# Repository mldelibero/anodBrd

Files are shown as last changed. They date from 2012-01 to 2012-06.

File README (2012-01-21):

This repo houses all of the important resources for the anodization board research project. It is part of a larger project at Case Western Reserve University that is attempting to create ultra-high energy density capacitors.

There have sofar been two main authors on this project:

Steven Ehret:
    Board design and layout
Michael DeLibero:
    Board validation and analysis
    Firmware code
    PC UI and data processing

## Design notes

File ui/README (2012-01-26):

This code communicates to the Board via USB.

It is responsible for:

configuring test modes
starting tests
receiving and saving data during tests
stopping tests

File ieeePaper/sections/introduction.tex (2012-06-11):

\section{Introduction}

Capacitors with high energy and power are essential for efficient management of electrical power.  Order of magnitude increases are desired for energy and power density. This may be possible with new self-repairing titanate dielectric capacitors using high surface area doped titanium and doped zirconium-titanium.  Anodizing at DC voltages forms a uniform dielectric film of doped titanium. The energy density of this dielectric is estimated to be on the order of 150J/$cm^3$ \cite{tiSponge}. This and the volume fraction of dielectric determines the energy density of the capacitor.

One of the major problems plaguing titanium electrolytic capacitors has been their high leakage currents \cite{tiCharHag}. In order to further research into titanium capacitors, custom anodization instrumentation has been developed to anodize and characterize a large number of candidate titanium capacitor materials. This instrumentation was necessary because conventional systems do not have the necessary dynamic range (1A-1nA measurement) or repeatability needed in this application.

\subsection{Anodization Process and Requirements}

Anodization is the act of growing an oxide layer (dielectric) on top of a metal anode. Dielectrics are beneficial because they allow capacitors to store more energy for a given electric field \cite{cwruEncDie}. The anodization process is preformed by connecting a voltage or current source to an anode and a cathode and immersing them in an electrolyte solution as shown in Fig. ~\ref{fig:anodSetup}

\begin{figure}[here]
\centering
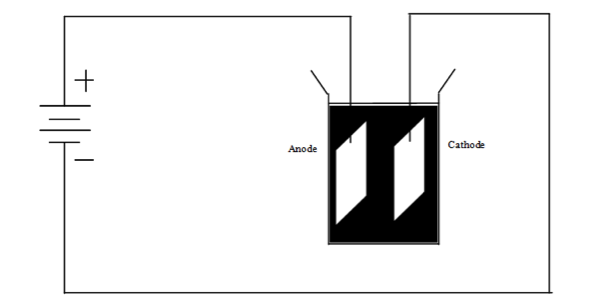
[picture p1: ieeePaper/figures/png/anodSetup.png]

\caption{Anodization Setup}
\label{fig:anodSetup}
\end{figure}

Referring to Fig. ~\ref{fig:anodSetup}, in the simplest case, the current transfer is an ionic transfer where the Ti anode reacts with $O_{2}$ to create a $TiO_{2}$ oxide layer. The reaction at the metal-oxide surface can be written as:

\begin{equation}
Ti + 0_2 => TiO_2 + 4e
\end{equation}
The titanium also reacts with the electrolyte solution to give off hydrogen:
\begin{equation}
Ti + 2H_20 => Ti0_2 + 4H
\end{equation}
This hydrogen reacts with the electrons at the cathode to create hydrogen gas and complete the ionic circuit.
\begin{equation}
4H + 4e => 2H_2
\end{equation}

This process is very similar to anodizing aluminum. For an explanation of that process visit \cite{cwruEncAlanod}.

Since the rate of oxide formation is dependent on the charge transport into the anode during anodization \cite{tiMinit}, a current source was selected. A typical anodization process with a current source will see the current and voltage progress as in Fig. ~\ref{fig:anodCurve}.

\begin{figure}[here]
\centering
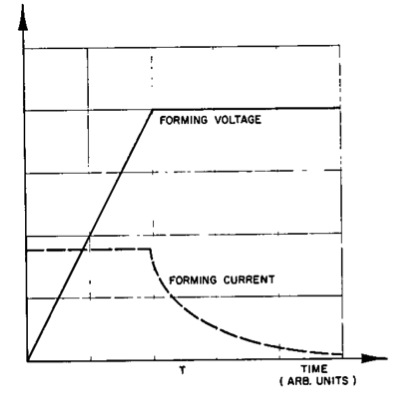
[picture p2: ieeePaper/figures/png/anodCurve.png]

\caption{Anodization Curve \cite{tiMinit}}
\label{fig:anodCurve}
\end{figure}

Our typical anodization tests work with a constant current of 20mA and a forming voltage of 30V. The anodization reaches the forming voltage in periods on the order of 30 seconds. The forming voltage then remains constant while the leakage current decreases over  a much longer time period (on the order of 24 hours) to currents on the order of 1 uA or less. The exact times and values are dependent upon the material and the size of the electrode.

If a constant current is introduced, the voltage will (ideally) rise linearly with time. This will happen until the anode reaches the compliance voltage, at which point the current through the DUT will begin to drop off until it reaches the leakage current of the unpackaged capacitor.

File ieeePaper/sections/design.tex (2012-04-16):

\begin{figure}[here]
\centering

\caption{Overall System Block Diagram}
\label{fig:blockDiagram}
\end{figure}

\subsection{Computer Control and Data Acquisition}

The user sets the test parameters of current, voltage compliance, and testing time. The anodization is then controlled by a set of Python scripts, which appropriately configure the hardware and control the data logging. Voltage and current measurements are sampled at a constant, high rate and all data is recorded. However, once the electrode has reached the forming voltage and the (leakage) current is slowly decreasing over time the data measurements are subsampled, and only a fraction of the sampled data is preserved.

\subsection{Current Source}

An ideal current source has the ability to output a constant, DC, current to any load with infinite voltage compliance. This ability makes a current source an attractive tool to use in anodization due to its ability to tightly control the rate of oxide growth on the anode.

\begin{figure}[here]
\centering
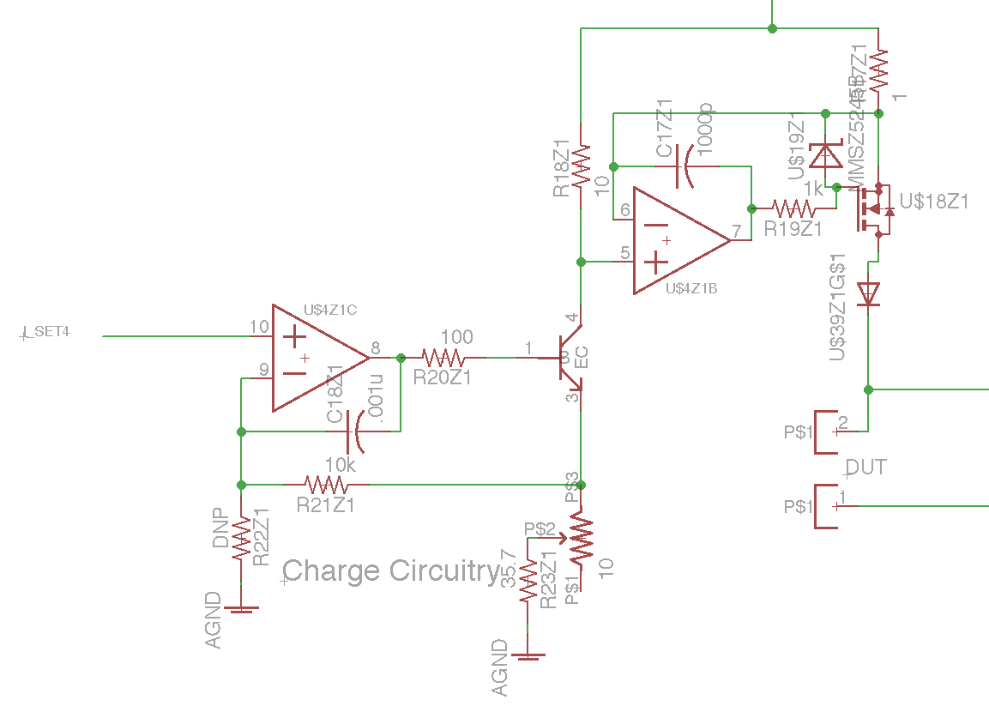
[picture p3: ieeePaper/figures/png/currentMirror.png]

\caption{Current Control Circuitry}
\label{fig:currentMirror}
\end{figure}

The current source implementation (Fig. ~\ref{fig:currentMirror}) was chosen around an op-amp based current mirror. The op-amp on the left, U4Z1C, is used to set and regulate the current through R23. This current functions as the reference current on the left leg of the current mirror. The op-amp on the right, U4Z1B, forces the voltage drop across $R_{17}$ and $R_{18}$ to be the same, causing the current in the right leg to go as:

\begin{equation}
I_2 = I_1*R_{18}/R_{17}
\end{equation}

With the values chosen in this design, this equates to a 10x current amplification from the reference to the current output. The adjustable supply voltage is applied to the node connecting resistors $R_{17}$ and $R_{18}$. The current source will be able supply a constant current up to an effective compliance voltage of the supply voltage minus the voltage drops of $R_{17}$, the pass transistor, and the protection diode.

The real current source has several practical limitations that provide less than ideal performance. 

\begin{enumerate}
\item Pass transistor power rating
\item Digitization of current settings
\item Slight nonlinearity due to the pass diode
\end{enumerate}

\begin{figure}[here]
\centering
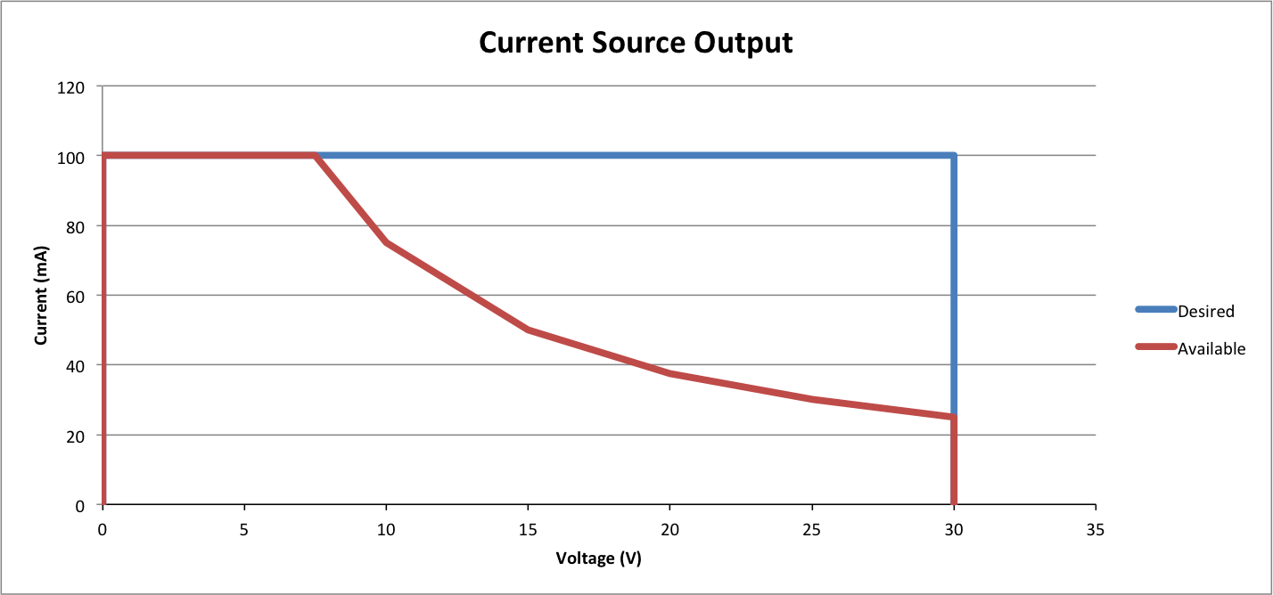
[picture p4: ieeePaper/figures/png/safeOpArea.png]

\caption{Current Source: Safe Operating Area}
\label{fig:safeOpArea}
\end{figure}

The safe operating area (Fig.  ~\ref{fig:safeOpArea}) is smaller than the desired operating output of 30V at 100mA. This difference comes from the limitations in the power dissipation of the pass transistor, U18Z1, in Fig. ~\ref{fig:currentMirror}. Assuming the worse case scenario of a short on the output, the allowable output current for a given voltage compliance can be found as:

\begin{equation}
I_{out} = P_{rating} / V_{comp}
\end{equation}

The current source operates by controlling the gate voltage of U18Z1 in Fig. ~\ref{fig:currentMirror}) ensure a constant current as the voltage on the DUT changes. Ideally, the source would be able to respond to a change in load impedance instantaneous to keep the current output constant. The real current source of Fig. ~\ref{fig:currentMirror} is limited by the Gain Bandwidth Product of the U4X1B (1.8Mhz). This limitation is of little concern, as the op-amp is still much faster then the fastest load change expected (See Section:\ref{DUT})

The ideal current source has the ability to output any desired current over its range with infinite precision. The current source in this design is limited in this regard by the discretization error of setting the current. Referring to (Fig. ~\ref{fig:currentMirror}) the signal $i_{set4}$ is used as a control signal to set the reference current in the device. This signal is controlled by a Microchip MCP4812 10-bit DAC. A first approximation of the discretization uncertainty in selecting DAC outputs can be found by:

\begin{equation}
U = Vi_{set} /(2n-1) / (R_{23} + R_{pot}) *(R_{18}/R_{17})
\end{equation}

Which yields an uncertainty in the current output of +/- 0.5mA. Calibration can eliminate this error for a single current output, but all other outputs will be in error by as much as the uncertainty.

The protection diode, U39, in (Fig. ~\ref{fig:currentMirror}) has the effect of increasing the voltage compliance as the current drops off after anodization. Looking at a standard diode curve, the voltage drop across the diode is roughly a constant 0.7V for high currents and exponentially diminishes towards zero as the current decreases. The tests are designed to not only anodize, but also continue to measure the long-term leakage current afterwards. This means that the current draw will decrease to the nA range, causing the effective voltage compliance to increase to about a diode drop above its anodization level. This affect will need to be considered during the analysis of the anodization data.

\subsection{DUT}
\label{DUT}

The device under test is typically a titanium anode to be anodized or a titanium capacitor. The device is able to operate with resistive loads and any capacitive loads (with capacitance large enough for the system to be able to respond.

\subsection{Current and Voltage Measurements}
\label{Current and Voltage Measurements}

The second part of the instrumentation is the measurement circuitry. An ideal measurement system would have no error or time delay when measuring the signal. It would also be able to perfectly reconstruct the signal for post analysis. 

\begin{figure}[here]
\centering
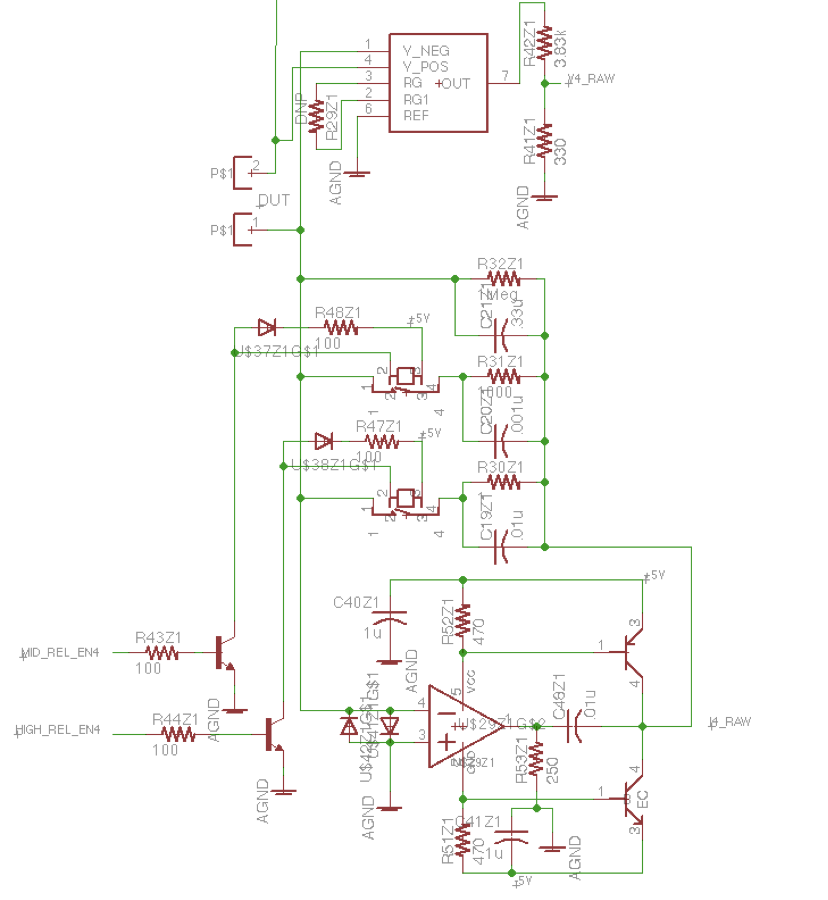
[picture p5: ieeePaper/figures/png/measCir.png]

\caption{Measurement Circuitry}
\label{fig:measCir}
\end{figure}

The measurement circuitry (Fig. ~\ref{fig:measCir}) implemented consists of two different parts, voltage and current measurements. The voltage of the DUT is measured differentially by an Analog Device’s AD8220 JFET instrumentation amplifier. This output is scaled and then sent to a 12-bit DAC. The current through the DUT is measure from a low side measurement topology known and a transimpedance amplifier. The amplifier creates a virtual ground at the negative terminal of the op-amp, U39, that allows for a current reading without subjecting the measurement circuitry to a high voltage and without floating the bottom of the DUT above ground.

Since it is desirable the measure both the anodization current and the leakage current, a basic transimpedance amplifier design was modified to include three switched feedback paths. This allows the current measurement to measure currents over eight orders of magnitude. The circuitry can handle currents from 10nA to 100mA. The three current ranges are listed in Table:~\ref{tab:dacRes}.

The real measurement circuitry has several practical limitations that limit it from performing ideally. Both the differential amplifier and the transimpedance amplifier send their signals to 6-pole Sallen-Key filters. These filters have a cutoff frequency of 10kHz\cite{sThesis} in order to filter out high frequency harmonics and other undesirable noise. Any signals higher than this will be severely attenuated in the captured data.

The DACs inject digitization errors into the measurement signals. They are able to measure signals with resolutions shown in Table:~\ref{tab:dacRes}.

\begin{table}[here]
\renewcommand{\arraystretch}{1.3}
\caption{DAC Resolution}
\label{tab:dacRes}
\centering
\begin{tabular}{c|c|c}
\hline
\bfseries Resolution & \bfseries Full Scale Measurement & \bfseries Comment\\
\hline\hline
7.32mV & 30V & \\
\hline
.098mA & 100mA & Hi Current (1A-1mA)\\
\hline
.98uA & 1mA & Med Current (1mA-1uA) \\
\hline
.98nA & 1uA & Lo Current (1uA-1nA)\\
\hline
\end{tabular}
\end{table}

Once the data is collected by the microcontroller, it is sent to a PC via USB for further analysis. The data is sampled by the ADCs at a configurable baud rate and transferred to the PC at a rate of 2Mbaud. This allows for maximum flexibility on the PC side, where any data coming in at a rate greater than what is desired can simply be discarded.

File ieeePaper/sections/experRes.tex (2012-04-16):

\section{Experimental Results}
Typical results from early materials can be found it Fig. 7. For additional data and complete testing curves, see \cite{sThesis} and \cite{mThesis}.

Since the circuitry has control over the output current and compliance voltage, it sets a limit for the maximum power allowed to be dissipated in its last pass transistor. This worst case operating method ensures that data taken of an unknown device will not damage the circuitry.
\begin{figure}[here]
\centering
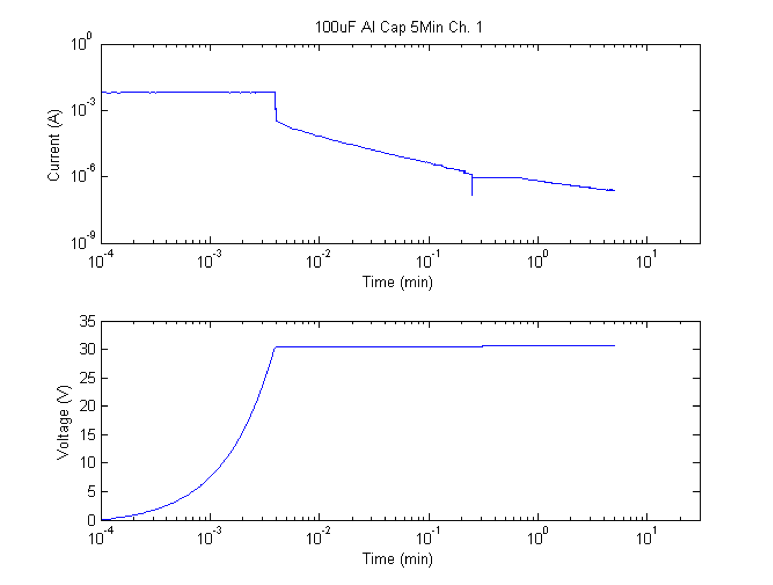
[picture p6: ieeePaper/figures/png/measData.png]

\caption{Typical Results}
\label{fig:measData}
\end{figure}

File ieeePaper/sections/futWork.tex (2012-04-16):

\section{Future Work}

Although this circuit functions to within its desired specifications, there are several improvements that can be made to achieve tighter control and greater accuracy.

\subsection{Safe Operating Area}

As discussed in Section:\ref{Current and Voltage Measurements} and seen in Fig:\ref{fig:safeOpArea}, the safe operating area of this circuitry is less then ideal. Even though the safe operating area contains the most commonly desired output conditions in the discussed experiments (20mA at 30V), it will need to be increased to accommodate higher current outputs.

A proposed way to achieve this increase is to create a software control loop using the existing circuitry. If the microcontroller limits the power dissipated in the last pass transistor while not affecting the DUT, this system can achieve a much greater safe operating area. Since the voltage across and current through the last pass transistor can be known at all times, power can be limited by the circuitry. The voltage at the top of the pass transistor can be estimated to be the compliance voltage set by the circuitry. During circuit operation, the voltage at the bottom of the pass transistor and current through are continuously measured by the microcontroller. Since anodization curves change on the order of $1 V/s$ (30V in 30 seconds), it is feasible to do a software controlled compensation loop. The microcontroller can set a constant current and ramp up the compliance voltage just above the voltage load. This will minimize the power dissipated in the last pass transistor and greatly increase the safe operating area of the circuitry.

\subsection{Schematic}

There are several improvements that could be made to the current schematic that would improve the overall design of the system. The circuitry uses 3 pass transistors with the last one transistor being undersized. The compliance voltage section could be redesigned in order to lower the number of pass elements and increase their power ratings. This will let the device supply currents to a wider variety of loads, without needing to use the technique described in the previous section.

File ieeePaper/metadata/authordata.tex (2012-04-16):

\newcommand{\gettitle}{Instrumentation For The Anodization and Characterization of Titanium Electrodes for Electrolytic Capacitors}

\newcommand{\getauthor}{M. DeLibero, Student Member, IEEE, S. Ehret, Member, IEEE, and F. Merat, Senior Member, IEEE}

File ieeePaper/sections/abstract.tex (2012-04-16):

\begin{abstract}
This paper presents a custom circuit for controlling the anodization of titanium capacitors and characterizing their performance. The circuitry provides a constant current source of 0-100mA up to a compliance voltage of 30V. The system can monitor and record leakage currents down to 10 nA over periods of up to 24 hours. Typical results obtained using sputtered titanium-zirconium capacitors are presented.
\end{abstract}

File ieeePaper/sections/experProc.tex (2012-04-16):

\section{Experimental Procedure}
The experimental setup to anodize the anode of a titanium capacitor with the aforementioned circuitry is as follows. The anode sample is prepared by cleaning the surface oxide off with a chemical bath. It is then placed in a beaker of anodizing solution. The current source is connected to the DUT and acts as both a current source and data logger until the test is finished and the current through the DUT has dropped to the leakage current.

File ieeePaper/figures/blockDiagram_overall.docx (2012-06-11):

DUT

PC

Current Source

Current Sense

Voltage Sense

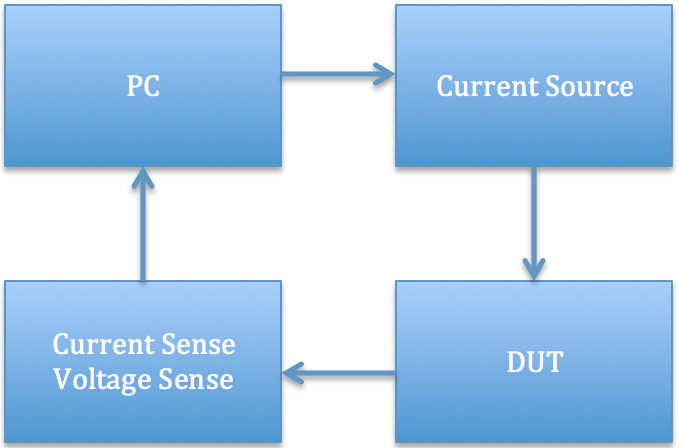
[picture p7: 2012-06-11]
ieeePaper/figures/blockDiagram.png

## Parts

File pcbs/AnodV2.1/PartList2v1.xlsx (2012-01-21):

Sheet: Digikey
Index | Quantity | Part Number | Value | Description | Customer Reference/Number Required per Board | Backorder Quantity | Unit Price | Extended Price |  | Need | Quantity
1 | 2 | 768-1101-1-ND (http://search.digikey.com/scripts/DkSearch/dksus.dll?Detail&itemSeq=102184557&uq=634458068631601009) |  | IC HS USB TO UART/FIFO 48LQFP | 1 | 0 | 4.25 | $8.50 | U5 | 2 | 2
2 | 5 | MCP4812-E/MS-ND (http://search.digikey.com/scripts/DkSearch/dksus.dll?Detail&itemSeq=102184565&uq=634458068631601009) |  | DAC 10BIT DUAL SPI/VREF 8MSOP | 4 | 0 | 2.3 | $11.50 |  | 0
3 | 8 | HE127-ND (http://search.digikey.com/scripts/DkSearch/dksus.dll?Detail&itemSeq=102184570&uq=634458068631601009) |  | RELAY REED SPST SIP SW 5V | 8 | 0 | 3.09 | $24.72 | U27 | 2 | 2
4 | 5 | NCP1117DT33GOS-ND (http://search.digikey.com/scripts/DkSearch/dksus.dll?Detail&itemSeq=102184588&uq=634458068631601009) |  | IC REG LDO 3.3V DPAK | 1 | 0 | 0.52 | $2.60 | U | 0
5 | 4 | AD8638ARJZ-REEL7CT-ND (http://search.digikey.com/scripts/DkSearch/dksus.dll?Detail&itemSeq=102184594&uq=634458068631601009) |  | IC OPAMP CHOPPER R-R SOT23-5 | 4 | 0 | 3.81 | $15.24 | U | 0
6 | 10 | 490-2872-ND (http://search.digikey.com/scripts/DkSearch/dksus.dll?Detail&itemSeq=102184612&uq=634458068631601009) |  | TRIMMER 10 OHM 0.5W TH | 8 | 0 | 1.07 | $10.70 | no longer used
7 | 10 | DMN3115UDMDICT-ND (http://search.digikey.com/scripts/DkSearch/dksus.dll?Detail&itemSeq=102184617&uq=634458068631601009) |  | MOSFET N-CH 30V 3.2A SOT-26 | 4 | 0 | 0.462 | $4.62 | U24,DS31187 | 0
8 | 10 | 296-7423-1-ND (http://search.digikey.com/scripts/DkSearch/dksus.dll?Detail&itemSeq=102184623&uq=634458068631601009) |  | IC OPAMP GP 635KHZ QUAD 14TSSOP | 8 | 0 | 1.17 | $11.70 |  | 0
9 | 4 | AD8220ARMZ-ND (http://search.digikey.com/scripts/DkSearch/dksus.dll?Detail&itemSeq=102184630&uq=634458068631601009) |  | IC AMP INST JFET R-R 15MA 8MSOP | 4 | 0 | 6.86 | $27.44 |  | 0
10 | 25 | ES1G-TPCT-ND (http://search.digikey.com/scripts/DkSearch/dksus.dll?Detail&itemSeq=102184689&uq=634458068631601009) |  | DIODE FAST REC 1A 400V DO214AC | 18 | 0 | 0.302 | $7.55 | U38 | 0
11 | 3 | ZXRE1004DFCT-ND (http://search.digikey.com/scripts/DkSearch/dksus.dll?Detail&itemSeq=102184694&uq=634458068631601009) |  | IC VREF 1.22V 20MA 1% SOT23-3 | 1 | 0 | 1.33 | $3.99 |  | 0
12 | 2 | CTX691CT-ND (http://search.digikey.com/scripts/DkSearch/dksus.dll?Detail&itemSeq=102184701&uq=634458068631601009) |  | OSC CLOCK 16.000000 MHZ 3.3V SMD | 1 | 0 | 3.92 | $7.84 |  | 0
13 | 1 | 285-1822-ND (http://search.digikey.com/scripts/DkSearch/dksus.dll?Detail&itemSeq=102184707&uq=634458068631601009) |  | POWER SUPPLY 36V 1.4A SGL OUTPUT | 1 | 0 | 29.93 | $29.93 |  | 0
14 | 5 | 296-21390-1-ND (http://search.digikey.com/scripts/DkSearch/dksus.dll?Detail&itemSeq=102184724&uq=634458068631601009) |  | IC VOLT REG POS ADJ 1.5A D2PAK-3 | 1 | 0 | 1.06 | $5.30 |  | 0
15 | 5 | LP38690DT-5.0-ND (http://search.digikey.com/scripts/DkSearch/dksus.dll?Detail&itemSeq=102184731&uq=634458068631601009) |  | IC REG LDO 1A 5.0V TO-252 | 1 | 0 | 1.64 | $8.20 |  | 0
16 | 2 | CP-1060-ND (http://search.digikey.com/scripts/DkSearch/dksus.dll?Detail&itemSeq=102184739&uq=634458068631601009) |  | CONN CIRCULAR DIN 6 PIN MALE | 1 | 0 | 1.6 | $3.20 |  | 0
17 | 2 | CP-2360-ND (http://search.digikey.com/scripts/DkSearch/dksus.dll?Detail&itemSeq=102184745&uq=634458068631601009) |  | CONN DIN 6 PIN FEMALE PCB | 1 | 0 | 1.37 | $2.74 |  | 0
18 | 5 | LM2990S-5.0-ND (http://search.digikey.com/scripts/DkSearch/dksus.dll?Detail&itemSeq=102184747&uq=634458068631601009) |  | IC REGULATOR NEG LDO TO-263 | 1 | 0 | 3.58 | $17.90 |  | 0
19 | 20 | 490-1718-1-ND (http://search.digikey.com/scripts/DkSearch/dksus.dll?Detail&itemSeq=102185015&uq=634458068631601009) |  | CAP CER 10UF 6.3V 20% X5R 0805 |  | 0 | 0.227 | $4.54 |  | 0
20 | 10 | SI2319DS-T1-E3CT-ND (http://search.digikey.com/scripts/DkSearch/dksus.dll?Detail&itemSeq=102185021&uq=634458068631601009) |  | MOSFET P-CH 40V 2.3A SOT23-3 | 8 | 0 | 0.86 | $8.60 | U18 | 5 | 5
21 | 12 | 2SD1758TLRCT-ND (http://search.digikey.com/scripts/DkSearch/dksus.dll?Detail&itemSeq=102185024&uq=634458068631601009) |  | TRANS NPN 32V 2A SOT-428 | 12 | 0 | 0.77 | $9.24 | U54 | 4 | 4
22 | 4 | 2SB1182TLRCT-ND (http://search.digikey.com/scripts/DkSearch/dksus.dll?Detail&itemSeq=102185030&uq=634458068631601009) |  | TRANSISTOR PNP 32V 2A SOT-428 | 4 | 0 | 1.05 | $4.20 | U55 | 4 | 4
23 | 10 | 493-1341-ND (http://search.digikey.com/scripts/DkSearch/dksus.dll?Detail&itemSeq=102185033&uq=634458068631601009) | 100 uF | CAP ALUM 100UF 50V 20% RADIAL | 3 | 0 | 0.215 | $2.15 |  | 0
24 | 50 | 490-1496-1-ND (http://search.digikey.com/scripts/DkSearch/dksus.dll?Detail&itemSeq=102185041&uq=634458068631601009) | 1200 pF | CAP CER 1200PF 50V 10% X7R 0603 |  | 0 | 0.054 | $2.70 |  | 0
25 | 50 | 445-5189-1-ND (http://search.digikey.com/scripts/DkSearch/dksus.dll?Detail&itemSeq=102202420&uq=634458100422898435) | 15000 pF | CAP CER 15000PF 50V X7R 0603 | 8 | 0 | 0.0376 | $1.88 | C55 | 0
26 | 100 | 490-1512-1-ND (http://search.digikey.com/scripts/DkSearch/dksus.dll?Detail&itemSeq=102185106&uq=634458068631601009) | 10000 pF | CAP CER 10000PF 50V 10% X7R 0603 |  | 0 | 0.015 | $1.50 |  | 0
27 | 250 | 490-1494-1-ND (http://search.digikey.com/scripts/DkSearch/dksus.dll?Detail&itemSeq=102185111&uq=634458068631601009) | 1000 pF | CAP CER 1000PF 50V 10% X7R 0603 |  | 0 | 0.01196 | $2.99 |  | 0
28 | 100 | 490-1500-1-ND (http://search.digikey.com/scripts/DkSearch/dksus.dll?Detail&itemSeq=102185121&uq=634458068631601009) | 2200 pF | CAP CER 2200PF 50V 10% X7R 0603 |  | 0 | 0.0283 | $2.83 |  | 0
29 | 250 | 490-1568-1-ND (http://search.digikey.com/scripts/DkSearch/dksus.dll?Detail&itemSeq=102185126&uq=634458068631601009) | .1 uF | CAP CER .1UF 50V Y5V 0603 |  | 0 | 0.01724 | $4.31 |  | 0
30 | 100 | 490-1543-1-ND (http://search.digikey.com/scripts/DkSearch/dksus.dll?Detail&itemSeq=102185132&uq=634458068631601009) | 1.0 uF | CAP CER 1.0UF 10V 10% X5R 0603 |  | 0 | 0.0336 | $3.36 |  | 0
31 | 10 | 445-5169-1-ND (http://search.digikey.com/scripts/DkSearch/dksus.dll?Detail&itemSeq=102185141&uq=634458068631601009) | 3.3 uF | CAP CER 3.3UF 10V X5R 0603 |  | 0 | 0.33 | $3.30 | C14 | 5 | 5
32 | 2 | 929400E-01-36-ND (http://search.digikey.com/scripts/DkSearch/dksus.dll?Detail&itemSeq=102185148&uq=634458068631601009) |  | CONN HEADER .100 SNGL STR 36POS | 18 | 0 | 1.8 | $3.60 |  | 0
33 | 10 | 587-1603-1-ND (http://search.digikey.com/scripts/DkSearch/dksus.dll?Detail&itemSeq=102185154&uq=634458068631601009) | 10 uH | INDUCTOR 10UH 20% 0805 SMD | 1 | 0 | 0.188 | $1.88 |  | 0
34 | 10 | 240-2370-1-ND (http://search.digikey.com/scripts/DkSearch/dksus.dll?Detail&itemSeq=102185159&uq=634458068631601009) |  | FERRITE 1A 60 OHM 0603 SMD | 4 | 0 | 0.081 | $0.81 |  | 0
35 | 20 | MMSZ5245B-TPMSCT-ND (http://search.digikey.com/scripts/DkSearch/dksus.dll?Detail&itemSeq=102185163&uq=634458068631601009) |  | DIODE ZENER 500MW 15V SOD123 | 12 | 0 | 0.255 | $5.10 | U33, | 0
36 | 30 | DSS4140UDICT-ND (http://search.digikey.com/scripts/DkSearch/dksus.dll?Detail&itemSeq=102185170&uq=634458068631601009) |  | TRANS BIPOLAR NPN 40V SOT-323 | 20 | 0 | 0.4 | $12.00 | U17 | 0
37 | 10 | 497-1958-1-ND (http://search.digikey.com/scripts/DkSearch/dksus.dll?Detail&itemSeq=102185182&uq=634458068631601009) |  | IC AMP QUAD BIPOLAR OP LP 14SOIC | 4 | 0 | 0.986 | $9.86 |  | 0
38 | 10 | RFD3055LE-ND (http://search.digikey.com/scripts/DkSearch/dksus.dll?Detail&itemSeq=102185192&uq=634458068631601009) |  | MOSFET N-CH 60V 11A I-PAK | 4 | 0 | 0.702 | $7.02 |  | 0
39 | 10 | WSLB-.10CT-ND (http://search.digikey.com/scripts/DkSearch/dksus.dll?Detail&itemSeq=102185200&uq=634458068631601009) | 0.10 O | RES .10 OHM 1/4W 1% 0805 SMD |  | 0 | 0.91 | $9.10 |  | 0
40 | 10 | RMCF0603FT1R00CT-ND (http://search.digikey.com/scripts/DkSearch/dksus.dll?Detail&itemSeq=102185208&uq=634458068631601009) | 1 O | RES TF 1 OHM 1% 0.1W 0603 |  | 0 | 0.025 | $0.25 | no longer used | 0
41 | 10 | P10.0HCT-ND (http://search.digikey.com/scripts/DkSearch/dksus.dll?Detail&itemSeq=102185213&uq=634458068631601009) | 10.0 O | RES 10.0 OHM 1/10W 1% 0603 SMD |  | 0 | 0.04 | $0.40 |  | 0
42 | 100 | P100HCT-ND (http://search.digikey.com/scripts/DkSearch/dksus.dll?Detail&itemSeq=102185215&uq=634458068631601009) | 100 O | RES 100 OHM 1/10W 1% 0603 SMD |  | 0 | 0.0105 | $1.05 |  | 0
43 | 50 | P330HCT-ND (http://search.digikey.com/scripts/DkSearch/dksus.dll?Detail&itemSeq=102185220&uq=634458068631601009) | 330 O | RES 330 OHM 1/10W 1% 0603 SMD |  | 0 | 0.0138 | $0.69 |  | 0
44 | 50 | P10.0KHCT-ND (http://search.digikey.com/scripts/DkSearch/dksus.dll?Detail&itemSeq=102185222&uq=634458068631601009) | 10.0 kO | RES 10.0K OHM 1/10W 1% 0603 SMD |  | 0 | 0.0138 | $0.69 |  | 0
45 | 50 | P100KHCT (http://search.digikey.com/scripts/DkSearch/dksus.dll?Detail&itemSeq=102185223&uq=634458068631601009) | 100 kO | RES 100K OHM 1/10W 1% 0603 SMD |  | 0 | 0.0138 | $0.69 |  | 0
46 | 10 | P12.0KHCT-ND (http://search.digikey.com/scripts/DkSearch/dksus.dll?Detail&itemSeq=102185237&uq=634458068631601009) | 12.0 kO | RES 12.0K OHM 1/10W 1% 0603 SMD |  | 0 | 0.04 | $0.40 |  | 0
47 | 50 | P124HCT-ND (http://search.digikey.com/scripts/DkSearch/dksus.dll?Detail&itemSeq=102185243&uq=634458068631601009) | 124 O | RES 124 OHM 1/10W 1% 0603 SMD |  | 0 | 0.0138 | $0.69 |  | 0
48 | 50 | P294HCT-ND (http://search.digikey.com/scripts/DkSearch/dksus.dll?Detail&itemSeq=102185248&uq=634458068631601009) | 294 O | RES 294 OHM 1/10W 1% 0603 SMD |  | 0 | 0.0138 | $0.69 |  | 0
49 | 50 | P470HCT-ND (http://search.digikey.com/scripts/DkSearch/dksus.dll?Detail&itemSeq=102185253&uq=634458068631601009) | 470 O | RES 470 OHM 1/10W 1% 0603 SMD |  | 0 | 0.0138 | $0.69 |  | 0
50 | 50 | P249HCT-ND (http://search.digikey.com/scripts/DkSearch/dksus.dll?Detail&itemSeq=102185257&uq=634458068631601009) | 249 O | RES 249 OHM 1/10W 1% 0603 SMD |  | 0 | 0.0138 | $0.69 |  | 0
51 | 50 | P14.7KHCT-ND (http://search.digikey.com/scripts/DkSearch/dksus.dll?Detail&itemSeq=102185260&uq=634458068631601009) | 14.7 kO | RES 14.7K OHM 1/10W 1% 0603 SMD |  | 0 | 0.0138 | $0.69 |  | 0
52 | 50 | P14.0KHCT-ND (http://search.digikey.com/scripts/DkSearch/dksus.dll?Detail&itemSeq=102185263&uq=634458068631601009) | 14.0 kO | RES 14.0K OHM 1/10W 1% 0603 SMD |  | 0 | 0.0138 | $0.69 |  | 0
53 | 50 | P1.00KHCT-ND (http://search.digikey.com/scripts/DkSearch/dksus.dll?Detail&itemSeq=102185266&uq=634458068631601009) | 1.00 kO | RES 1.00K OHM 1/10W 1% 0603 SMD |  | 0 | 0.0138 | $0.69 |  | 0
54 | 50 | P20.5KHCT-ND (http://search.digikey.com/scripts/DkSearch/dksus.dll?Detail&itemSeq=102185268&uq=634458068631601009) | 20.5 kO | RES 20.5K OHM 1/10W 1% 0603 SMD |  | 0 | 0.0138 | $0.69 |  | 0
55 | 50 | P2.94KHCT-ND (http://search.digikey.com/scripts/DkSearch/dksus.dll?Detail&itemSeq=102185272&uq=634458068631601009) | 2.94 kO | RES 2.94K OHM 1/10W 1% 0603 SMD |  | 0 | 0.0138 | $0.69 | R69 | 0
56 | 50 | P3.57KHCT-ND (http://search.digikey.com/scripts/DkSearch/dksus.dll?Detail&itemSeq=102185277&uq=634458068631601009) | 3.57 kO | RES 3.57K OHM 1/10W 1% 0603 SMD |  | 0 | 0.0138 | $0.69 | R72 | 0
57 | 50 | P10.2KHCT-ND (http://search.digikey.com/scripts/DkSearch/dksus.dll?Detail&itemSeq=102185281&uq=634458068631601009) | 10.2 kO | RES 10.2K OHM 1/10W 1% 0603 SMD |  | 0 | 0.0138 | $0.69 |  | 0
58 | 50 | P35.7HCT-ND (http://search.digikey.com/scripts/DkSearch/dksus.dll?Detail&itemSeq=102185286&uq=634458068631601009) | 35.7 O | RES 35.7 OHM 1/10W 1% 0603 SMD |  | 0 | 0.0138 | $0.69 |  | 0
59 | 50 | P68.1HCT-ND (http://search.digikey.com/scripts/DkSearch/dksus.dll?Detail&itemSeq=102185295&uq=634458068631601009) | 68.1 O | RES 68.1 OHM 1/10W 1% 0603 SMD |  | 0 | 0.0138 | $0.69 |  | 10 | 10
60 | 50 | P2.00KHCT-ND (http://search.digikey.com/scripts/DkSearch/dksus.dll?Detail&itemSeq=102185299&uq=634458068631601009) | 2.00 kO | RES 2.00K OHM 1/10W 1% 0603 SMD |  | 0 | 0.0138 | $0.69 |  | 0
61 | 50 | P3.83KHCT-ND (http://search.digikey.com/scripts/DkSearch/dksus.dll?Detail&itemSeq=102185302&uq=634458068631601009) | 3.83k | RES 3.83K OHM 1/10W 1% 0603 SMD |  | 0 | 0.0138 | $0.69 |  | 0
62 | 50 | P4.42KHCT-ND (http://search.digikey.com/scripts/DkSearch/dksus.dll?Detail&itemSeq=102185309&uq=634458068631601009) | 4.42 kO | RES 4.42K OHM 1/10W 1% 0603 SMD |  | 0 | 0.0138 | $0.69 |  | 0
63 | 50 | P7.87KHCT-ND (http://search.digikey.com/scripts/DkSearch/dksus.dll?Detail&itemSeq=102185313&uq=634458068631601009) | 7.87 kO | RES 7.87K OHM 1/10W 1% 0603 SMD |  | 0 | 0.0138 | $0.69 |  | 0
64 | 50 | 541-3.57HHCT-ND (http://search.digikey.com/scripts/DkSearch/dksus.dll?Detail&itemSeq=102185316&uq=634458068631601009) | 3.57 O | RES 3.57 OHM 1/10W 1% 0603 SMD |  | 0 | 0.0436 | $2.18 |  | 0
65 | 1 | 151-1081-ND (http://search.digikey.com/scripts/DkSearch/dksus.dll?Detail&itemSeq=102185319&uq=634458068631601009) |  | CONN USB JACK TYPE B HORIZON R/A | 1 | 0 | 0.96 | $0.96 |  | 0
66 | 10 | 478-4086-1-ND (http://search.digikey.com/scripts/DkSearch/dksus.dll?Detail&itemSeq=102185485&uq=634458068631601009) | 10uF | CAP TANT LOWESR 10UF 10V 20% SMD | 2 | 0 | 0.326 | $3.26 | C1, C3 | 5 | 5
67 | 5 | SW336-ND (http://search.digikey.com/scripts/DkSearch/dksus.dll?Detail&itemSeq=102201465&uq=634458068631601009) |  | SWITCH SLIDE 3P 3POS EYELET TERM | 1 |  |  |  |  | 0
68 |  | P1.00MHCT-ND (http://search.digikey.com/us/en/products/ERJ-3EKF1004V/P1.00MHCT-ND/198072) | 1 MO | RES 1.00M OHM 1/10W 1% 0603 SMD | 2 |  |  |  | R32 | 0
69 |  | 490-3294-1-ND | .33 uF | Cap CER .33uF |  |  |  |  | C21 | 2 | 100
70 |  | P442HCT-ND (http://search.digikey.com/us/en/products/ERJ-3EKF4420V/P442HCT-ND/198392) | 442 O | RES 442 |  |  |  |  |  | 0
 |  | RHM9.10AECT-ND (http://search.digikey.com/us/en/products/ESR10EZPF9R10/RHM9.10AECT-ND/1983890) | 9.10 O | RES 9.10 OHM 1/4W 1% 0805 SMD | 2 |  |  |  | R30 | 10 | 10
 |  | 490-2943-ND |  | TRIMMER 50 OHM 0.5W TH | 8 |  |  |  | R23, R28 | 2 | 10

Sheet: DigiKey_order_12v16v2011
DigiKey Num | Quantity | Customer Reference | Description
SI2319DS-T1-E3CT-ND | 5 | U18 | MOSFET P-CH 40V 2.3A SOT23-3
RHM9.10AECT-ND | 10 | R30 | RES 9.10 OHM 1/4W 1% 0805 SMD
P68.1HCT-ND | 10 | 0 | RES 68.1 OHM 1/10W 1% 0603 SMD
HE127-ND | 2 | U27 | RELAY REED SPST SIP SW 5V
768-1101-1-ND | 2 | U5 | IC HS USB TO UART/FIFO 48LQFP
490-2943-ND | 10 | R23, R28 | TRIMMER 50 OHM 0.5W TH
490-3294-1-ND | 100 | C21 | Cap CER .33uF
478-4086-1-ND | 5 | C1, C3 | CAP TANT LOWESR 10UF 10V 20% SMD
445-5169-1-ND | 5 | C14 | CAP CER 3.3UF 10V X5R 0603
2SD1758TLRCT-ND | 4 | U54 | TRANS NPN 32V 2A SOT-428
2SB1182TLRCT-ND | 4 | U55 | TRANSISTOR PNP 32V 2A SOT-428

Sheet: Mouser
Remove | Product Detail |  | Customer Part # | Order Qty. |  | Price | Ext. | Number Required per Board
 |  |  |  |  |  | (USD) | (USD)
 | Mouser #: | 774-636L3I012M00000 (https://www.mouser.com/Search/ProductDetail.aspx) |  |  |  | $3.50 | $7.00 | 1
 | Mfr. #: | 636L3I012M00000 (https://www.mouser.com/Search/ProductDetail.aspx) |  | Packaging Choice: (https://www.mouser.com/Cart/MiniReelWithNoJavaScript.aspx)
 | Manufacturer: | CTS |  | Cut Tape
 | Desc.: | Standard Clock Oscillators 12MHz 3.3V 50ppm -40C +85C (https://www.mouser.com/Search/ProductDetail.aspx)
 | RoHS: | RoHS Compliant |  | Availability
 |  |  |  | 2 | Ships Now
 | Lifecycle: | New Product: New from this supplier.
 | Mouser #: | 645-598-8110-107F (https://www.mouser.com/Search/ProductDetail.aspx) |  |  |  | $0.10 | $1.00 | 4
 | Mfr. #: | 598-8110-107F (https://www.mouser.com/Search/ProductDetail.aspx) |  | Packaging Choice: (https://www.mouser.com/Cart/MiniReelWithNoJavaScript.aspx)
 | Manufacturer: | Dialight |  | Cut Tape
 | Desc.: | Standard LED - SMD Red Water Clr 80mcd 642nm (https://www.mouser.com/Search/ProductDetail.aspx)
 | RoHS: | RoHS Compliant |  | Availability
 |  |  |  | 10 | Ships Now
 | Mouser #: | 645-598-8160-107F (https://www.mouser.com/Search/ProductDetail.aspx) |  |  |  | $0.09 | $0.90 | 6
 | Mfr. #: | 598-8160-107F (https://www.mouser.com/Search/ProductDetail.aspx) |  | Packaging Choice: (https://www.mouser.com/Cart/MiniReelWithNoJavaScript.aspx)
 | Manufacturer: | Dialight |  | Cut Tape
 | Desc.: | Standard LED - SMD YelGrn Water Clr 60mcd 575nm (https://www.mouser.com/Search/ProductDetail.aspx)
 | RoHS: | RoHS Compliant |  | Availability
 |  |  |  | 10 | Ships Now
 | Mouser #: | 556-ATXMEGA64A3-AU (https://www.mouser.com/Search/ProductDetail.aspx) |  |  |  | $7.17 | $14.34 | 1
 | Mfr. #: | ATXMEGA64A3-AU (https://www.mouser.com/Search/ProductDetail.aspx)
 | Manufacturer: | Atmel |  | Availability
 | Desc.: | Microcontrollers (MCU) 8/16 bit 1.6V-3.6V 64KB + 4KB (https://www.mouser.com/Search/ProductDetail.aspx) |  | 2 | Ships Now
 | RoHS: | RoHS Compliant
 | Mouser #: | 579-93LC66BT-I/OT (https://www.mouser.com/Search/ProductDetail.aspx) |  |  |  | $0.28 | $0.56 | 1
 | Mfr. #: | 93LC66BT-I/OT (https://www.mouser.com/Search/ProductDetail.aspx) |  | Packaging Choice: (https://www.mouser.com/Cart/MiniReelWithNoJavaScript.aspx)
 | Manufacturer: | Microchip |  | Cut Tape
 | Desc.: | EEPROM 256x16 (https://www.mouser.com/Search/ProductDetail.aspx)
 | RoHS: | RoHS Compliant |  | Availability
 |  |  |  | 2 | Ships Now
 | Mouser #: | 845-SH02-5.08 (https://www.mouser.com/Search/ProductDetail.aspx) |  |  |  | $0.84 | $3.36 | 4 | May not need at all - depends how you want to connect wiring to external samples
 | Mfr. #: | SH02-5,08 (https://www.mouser.com/Search/ProductDetail.aspx)
 | Manufacturer: | Altech |  | Availability
 | Desc.: | Pluggable Terminal Blocks PCBPlug 5.08mm (https://www.mouser.com/Search/ProductDetail.aspx) |  | 4 | Ships Now
 | RoHS: | RoHS Compliant
 | Mouser #: | 845-PVP02-5.08 (https://www.mouser.com/Search/ProductDetail.aspx) |  |  |  | $0.24 | $0.96 | 4 | May not need at all - depends how you want to connect wiring to external samples
 | Mfr. #: | PVP02-5.08 (https://www.mouser.com/Search/ProductDetail.aspx)
 | Manufacturer: | Altech |  | Availability
 | Desc.: | Pluggable Terminal Blocks VerHead 5.08 ClEnd (https://www.mouser.com/Search/ProductDetail.aspx) |  | 4 | Ships Now
 | RoHS: | RoHS Compliant
 | Mouser #: | 556-ATAVRDRAGON (https://www.mouser.com/Search/ProductDetail.aspx) |  |  |  | $49.00 | $49.00
 | Mfr. #: | ATAVRDRAGON (https://www.mouser.com/Search/ProductDetail.aspx)
 | Manufacturer: | Atmel |  | Availability
 | Desc.: | Emulators / Simulators AVR Emulator and Progammer (https://www.mouser.com/Search/ProductDetail.aspx) |  | 1 | Ships Now
 | RoHS: | RoHS Compliant
For additional information on availability, click on the Mouser Part #. | MERCHANDISE TOTAL: | $77.12 (USD)
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

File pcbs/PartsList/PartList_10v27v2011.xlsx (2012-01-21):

Index | Quantity | Part Number | Description | Customer Reference | Backorder Quantity | Unit Price | Extended Price
1 | 5 | SI2319DS-T1-E3CT-ND (http://search.digikey.com/scripts/DkSearch/dksus.dll?Detail&itemSeq=106360572&uq=634553048154718234) | MOSFET P-CH 40V 2.3A SOT23-3 | U18 | 0 | 0.86 | $4.30
2 | 100 | RMCF0603FT1R00CT-ND (http://search.digikey.com/scripts/DkSearch/dksus.dll?Detail&itemSeq=106360573&uq=634553048154718234) | RES TF 1 OHM 1% 0.1W 0603 | R30 | 0 | 0.0105 | $1.05
3 | 100 | P442HCT-ND (http://search.digikey.com/scripts/DkSearch/dksus.dll?Detail&itemSeq=106360574&uq=634553048154718234) | RES 442 OHM 1/10W 1% 0603 SMD | R71 | 0 | 0.0105 | $1.05
4 | 100 | P2.94KHCT-ND (http://search.digikey.com/scripts/DkSearch/dksus.dll?Detail&itemSeq=106360575&uq=634553048154718234) | RES 2.94K OHM 1/10W 1% 0603 SMD | R69 | 0 | 0.0105 | $1.05
5 | 100 | P1.00MHCT-ND (http://search.digikey.com/scripts/DkSearch/dksus.dll?Detail&itemSeq=106360576&uq=634553048154718234) | RES 1.00M OHM 1/10W 1% 0603 SMD | R32 | 0 | 0.0105 | $1.05
6 | 2 | NCP1117DT33GOS-ND (http://search.digikey.com/scripts/DkSearch/dksus.dll?Detail&itemSeq=106360577&uq=634553048154718234) | IC REG LDO 3.3V DPAK | U | 0 | 0.52 | $1.04
7 | 8 | MMSZ5245B-TPMSCT-ND (http://search.digikey.com/scripts/DkSearch/dksus.dll?Detail&itemSeq=106360578&uq=634553048154718234) | DIODE ZENER 500MW 15V SOD123 | U33, | 0 | 0.38 | $3.04
8 | 3 | HE127-ND (http://search.digikey.com/scripts/DkSearch/dksus.dll?Detail&itemSeq=106360579&uq=634553048154718234) | RELAY REED SPST SIP SW 5V | U27 | 0 | 3.09 | $9.27
9 | 20 | ES1G-TPCT-ND (http://search.digikey.com/scripts/DkSearch/dksus.dll?Detail&itemSeq=106360580&uq=634553048154718234) | DIODE FAST REC 1A 400V DO214AC | U38 | 0 | 0.302 | $6.04
10 | 5 | AD8638ARJZ-REEL7CT-ND (http://search.digikey.com/scripts/DkSearch/dksus.dll?Detail&itemSeq=106360581&uq=634553048154718234) | IC OPAMP CHOPPER R-R SOT23-5 | U | 0 | 3.03 | $15.15
11 | 3 | 768-1101-1-ND (http://search.digikey.com/scripts/DkSearch/dksus.dll?Detail&itemSeq=106360582&uq=634553048154718234) | IC HS USB TO UART/FIFO 48LQFP | U5 | 0 | 4.25 | $12.75
12 | 100 | 490-1500-1-ND (http://search.digikey.com/scripts/DkSearch/dksus.dll?Detail&itemSeq=106360583&uq=634553048154718234) | CAP CER 2200PF 50V 10% X7R 0603 | C21 | 0 | 0.0283 | $2.83
13 | 5 | 2SD1758TLRCT-ND (http://search.digikey.com/scripts/DkSearch/dksus.dll?Detail&itemSeq=106360584&uq=634553048154718234) | TRANS NPN 32V 2A SOT-428 | U54 | 0 | 0.77 | $3.85
14 | 50 | 100XBK-ND (http://search.digikey.com/scripts/DkSearch/dksus.dll?Detail&itemSeq=106360860&uq=634553048154718234) | RES 100 OHM 1/4W 1% METAL FILM | Don | 0 | 0.091 | $4.55
15 | 75 | J151-ND (http://search.digikey.com/scripts/DkSearch/dksus.dll?Detail&itemSeq=106360886&uq=634553048154718234) | CONN JACK BANANA INSUL NYLON RED | Don-plugs | 0 | 0.585 | $43.88
16 | 4 | WM18699-ND (http://search.digikey.com/scripts/DkSearch/dksus.dll?Detail&itemSeq=106374887&uq=634553048154718234) | CONN RECEPT 8POS 2MM VERT SMD | CONN1 | 0 | 2 | $8.00
 |  |  |  |  |  | Subtotal | $118.90

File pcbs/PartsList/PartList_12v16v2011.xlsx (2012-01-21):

DigiKey Num | Quantity | Customer Reference | Description | Good
SI2319DS-T1-E3CT-ND | 5 | U18 | MOSFET P-CH 40V 2.3A SOT23-3 | 1
RHM9.10AECT-ND | 10 | R30 | RES 9.10 OHM 1/4W 1% 0805 SMD | 1
P68.1HCT-ND | 10 | 0 | RES 68.1 OHM 1/10W 1% 0603 SMD | 1
HE127-ND | 2 | U27 | RELAY REED SPST SIP SW 5V | 1
490-2943-ND | 10 | R23, R28 | TRIMMER 50 OHM 0.5W TH | 1
490-1500-1-ND | 100 | C21 | Cap CER .33uF | 1
478-4086-1-ND | 5 | C1, C3 | CAP TANT LOWESR 10UF 10V 20% SMD | 1
445-5169-1-ND | 5 | C14 | CAP CER 3.3UF 10V X5R 0603 | 1
2SD1758TLRCT-ND | 4 | U54 | TRANS NPN 32V 2A SOT-428 | 1
2SB1182TLRCT-ND | 4 | U55 | TRANSISTOR PNP 32V 2A SOT-428 | 1
 |  |  |  |  | 2011-12-16

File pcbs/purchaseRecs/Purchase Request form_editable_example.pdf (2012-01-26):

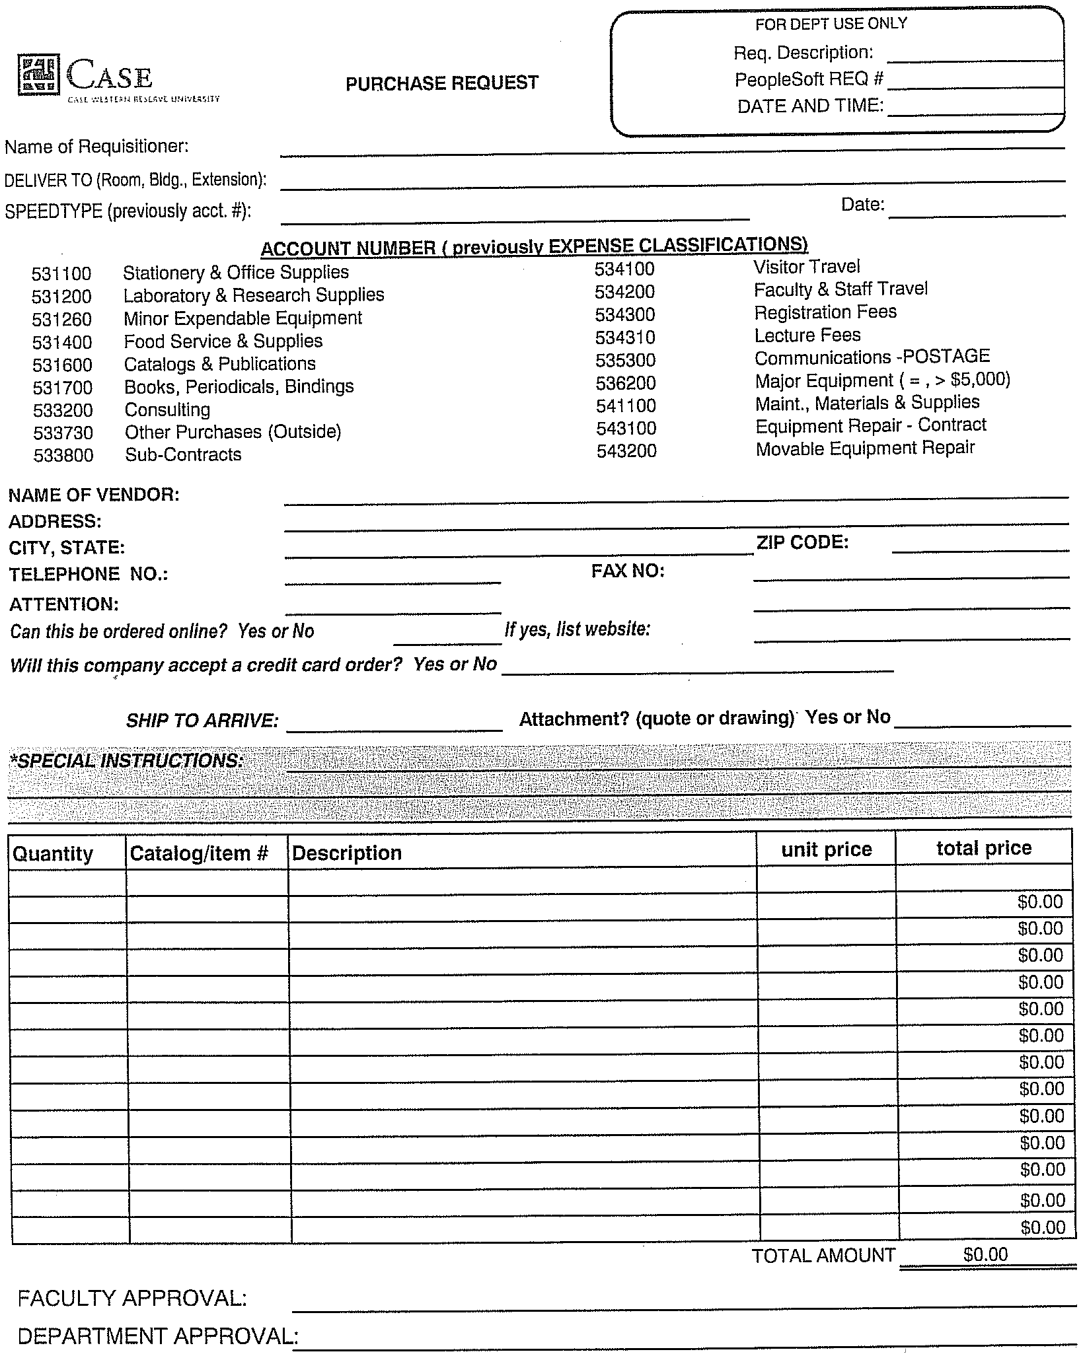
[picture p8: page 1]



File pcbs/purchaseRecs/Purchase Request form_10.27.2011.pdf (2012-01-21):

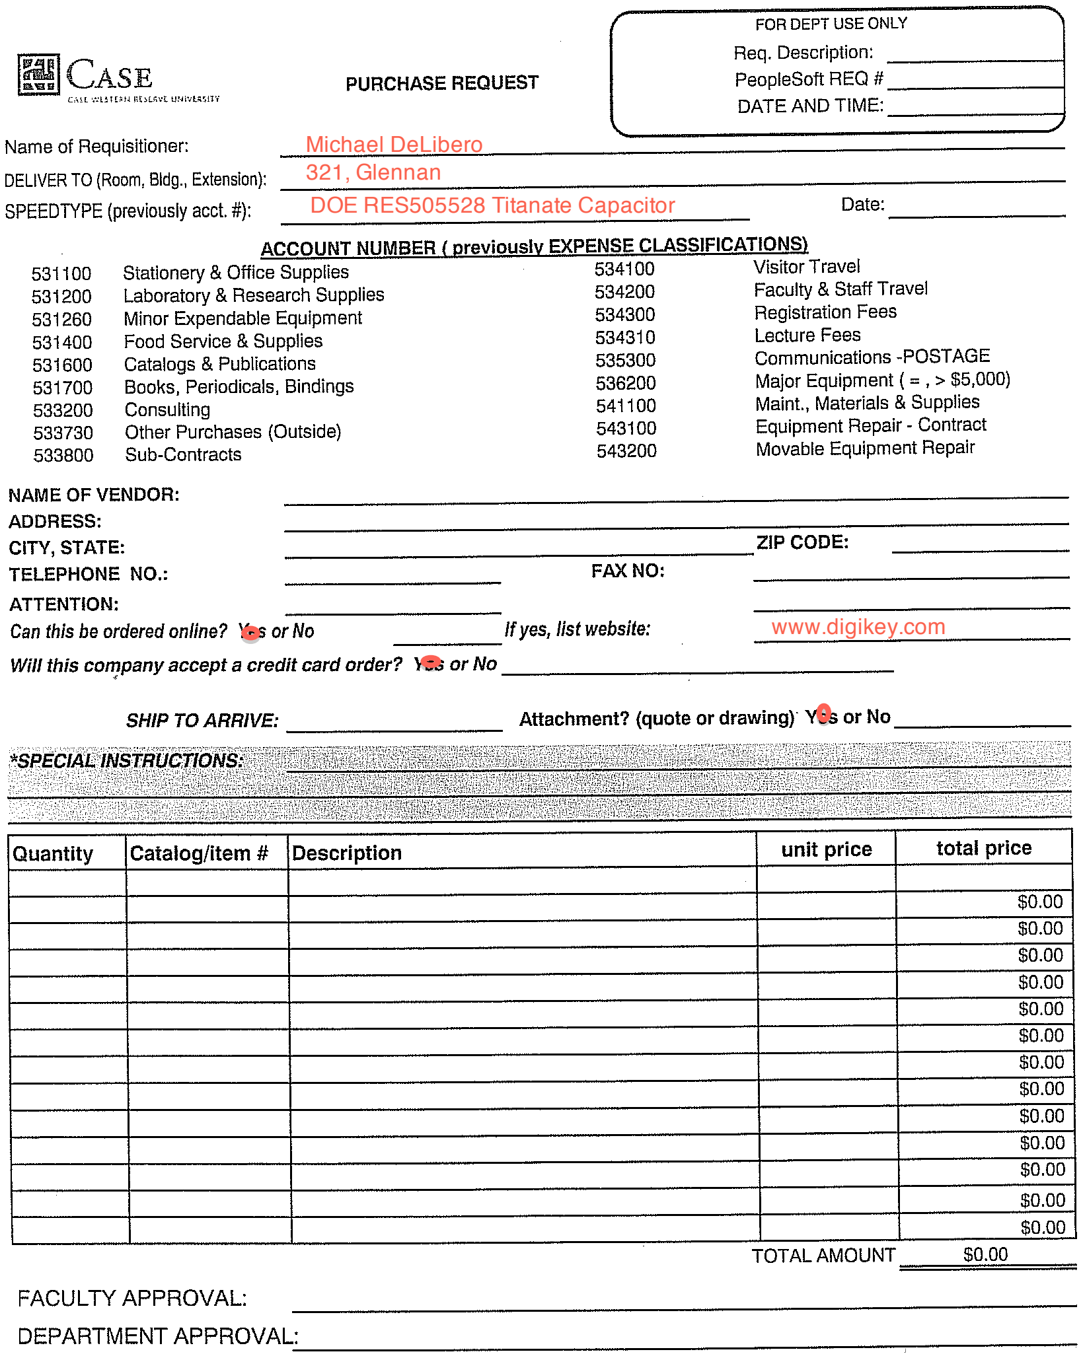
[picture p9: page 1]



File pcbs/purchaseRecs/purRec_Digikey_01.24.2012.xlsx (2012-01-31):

Part Number | Order | Cus Ref | Cost | Total Cost
MCP4812-E/MS-ND (http://search.digikey.com/scripts/DkSearch/dksus.dll?Detail&itemSeq=102184565&uq=634458068631601009) | 4 |  | $2.30 | $9.20
HE3351A0500 | 2 |  | $3.09 | $6.18
AD8638ARJZ-REEL7 | 1 |  | $3.03 | $3.03
TLC27M4IPWR | 4 | U43,U44 | $1.17 | $4.68
AD8220ARMZ-ND (http://search.digikey.com/scripts/DkSearch/dksus.dll?Detail&itemSeq=102184630&uq=634458068631601009) | 10 | U26-Diff amp | $6.42 | $64.20
ES1G-TP | 10 |  | $0.30 | $3.02
ZXRE1004DFCT-ND (http://search.digikey.com/scripts/DkSearch/dksus.dll?Detail&itemSeq=102184694&uq=634458068631601009) | 2 | U30 | $1.33 | $2.66
CTX691CT-ND (http://search.digikey.com/scripts/DkSearch/dksus.dll?Detail&itemSeq=102184701&uq=634458068631601009) | 2 | U32 | $3.92 | $7.84
CP-1060-ND (http://search.digikey.com/scripts/DkSearch/dksus.dll?Detail&itemSeq=102184739&uq=634458068631601009) | 2 |  | $1.84 | $3.68
CP-2360-ND (http://search.digikey.com/scripts/DkSearch/dksus.dll?Detail&itemSeq=102184745&uq=634458068631601009) | 2 |  | $1.57 | $3.14
SI2319DS-T1-E3 (http://search.digikey.com/scripts/DkSearch/dksus.dll?Detail&itemSeq=102185021&uq=634458068631601009) | 10 | U14,U18 | $0.84 | $8.40
587-1603-1-ND (http://search.digikey.com/scripts/DkSearch/dksus.dll?Detail&itemSeq=102185154&uq=634458068631601009) | 10 |  | $0.19 | $1.88
DSS4140U-7 | 10 | U16,U17,U34,U35,U36 | $0.40 | $4.00
MC33174DG | 3 | U4 | $1.58 | $4.74
151-1081-ND (http://search.digikey.com/scripts/DkSearch/dksus.dll?Detail&itemSeq=102185319&uq=634458068631601009) | 2 |  | $1.04 | $2.08
SW336-ND (http://search.digikey.com/scripts/DkSearch/dksus.dll?Detail&itemSeq=102201465&uq=634458068631601009) | 5 |  | $1.78 | $8.90
TPSA106M010R1800 | 4 |  | $0.60 | $2.40
PV36W500C01B00 | 5 |  | $1.36 | $6.80
1437671-1 | 4 | DUT conns | $1.13 | $4.52
ZXMP2120FFTA | 4 |  | $0.70 | $2.80
 |  |  |  | Total
 |  |  |  | 154.15

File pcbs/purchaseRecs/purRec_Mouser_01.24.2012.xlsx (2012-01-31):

Mfg Part Number | Quantity 1 | Description | Mouser Part Number | Stock | Lead Time | Min\Mult | RoHS | PB Free | Package Type | Package Quantity | NCNR | Price 1 | Mfg Name | Mfg Part Number | Mfg Name | Customer Part Number | Description | Quantity 2 | Quantity 3 | Quantity 4 | Quantity 5 | Price 2 | Price 3 | Price 4 | Price 5 | Package Price | Data Sheet URL | Lifecycle | MouseReel™ | Suggested Replacement | RoHS Replacement | Mouser Part Number
598-8160-107F | 4
579-93LC66BT | 1
ATXMEGA64A3-AU | 4

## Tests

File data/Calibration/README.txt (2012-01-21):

*11.30.2011
	These were the initial tests for ch1 and ch2 currents.

	The data in these tests is invalid due to 2s complement issues, but is kept
	here for recording purposes.
*12.01.2011
	Ch1 and Ch2 current calibration data. Use with GUI v2.5
						       board 2.1
						       firmware v3.0
	Hardware:
		Agilent E3631A Voltage Source (0-6V range)
		HP 34401A Current Meter

	***Ch1 broke at this point
	Ch2 lo current readings were taken with
	Keithley 2000 Multimeter

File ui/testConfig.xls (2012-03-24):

User Name | Michael DeLibero
Test Date | 2012-03-01
Anod Material | Titanium
Electrolye | H3PO4
Ch1 Vol(V) | 1
Ch1 Cur(mA) | 23
Ch1 Time(min) | 0.01428571429
Ch2 Vol(V) | 15
Ch2 Cur(mA) | 90
Ch2 Time(min) | 0.01639344262

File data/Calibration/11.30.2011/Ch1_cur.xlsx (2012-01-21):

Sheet: Ch1_cur.txt (root)
Root Name | Title | Author | Date/Time | Groups | Description
Ch1_cur.txt |  |  |  | 3
Group | Channels | Description | Anodization_Voltage | Anoidzation_Current | Board_Revision | Calibration_Version | Date_of_Testing | Electrolyte | GUI__Rev | Material | Researcher
Channel1 | 4 |  | 30.000000 | 100.000000 | 2.1 | 2.0 | 11/28/2011 | Liquid | 2.5 | Titanium | Michael DeLibero
Channel2 | 0 |  | 30.000000 | 100.000000 | 2.1 | 2.0 | 11/28/2011 | Liquid | 2.5 | Titanium | Michael DeLibero
Channel3 | 0 |  | 30.000000 | 100.000000 | 2.1 | 2.0 | 11/28/2011 | Liquid | 2.5 | Titanium | Michael DeLibero
Channel1
Channel | Datatype | Unit | Length | Minimum | Maximum | Description | NI_ArrayColumn | Start Index
Timestamp | DT_STRING |  | 82 |  |  |  | 0
Voltage | DT_STRING |  | 82 |  |  |  | 1
Current | DT_STRING |  | 82 |  |  |  | 2
Is | DT_STRING |  | 82 |  |  |  | 3
Channel2
Channel | Datatype | Unit | Length | Minimum | Maximum | Description | Start Index
Channel3
Channel | Datatype | Unit | Length | Minimum | Maximum | Description | Start Index

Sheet: Channel1
11/30/2011 | Voltage | Current | Is
17:17:34 | FBE0 | FE6C | -0.1952
17:17:35 | FBF4 | FE6C | -0.1952
17:17:38 | FBFF | FE6B | -0.1952
17:17:39 | FC09 | FE6B | -0.1952
17:17:39 | FC11 | FE6D | -0.1952
17:18:06 | FBE4 | 8 | 0.0043
17:18:07 | FBE0 | A | 0.0043
17:18:08 | FBE7 | A | 0.0043
17:18:09 | FBE2 | 9 | 0.0043
17:18:11 | FBDD | 8 | 0.0043
17:18:13 | FBD1 | 9 | 0.0043
17:18:15 | FBD0 | A | 0.0043
17:18:16 | FBD8 | 9 | 0.0043
17:18:17 | FBD1 | A | 0.0043
17:18:17 | FBCC | 9 | 0.0043
17:18:28 | FBD1 | 26C | 0.2976
17:18:44 | FBCB | 5B8 | 0.7053
17:18:46 | FBDE | 5B9 | 0.7053
17:18:47 | FBD5 | 5B9 | 0.7053
17:18:47 | FBD9 | 5B9 | 0.7053
17:18:48 | FBE4 | 5B9 | 0.7053
17:18:49 | FBD9 | 5B9 | 0.7053
17:18:49 | FBDB | 5B9 | 0.7053
17:18:49 | FBDE | 5BB | 0.7053
17:18:50 | FBE0 | 5B9 | 0.7053
17:18:50 | FBDA | 5B8 | 0.7053
17:18:50 | FBDE | 5B7 | 0.7053
17:18:50 | FBDD | 5B9 | 0.7053
17:18:51 | FBE1 | 5B8 | 0.7053
17:19:03 | FBEE | 68D | 0.8072
17:19:04 | FBE6 | 68D | 0.8072
17:19:06 | FBEB | 68B | 0.8072
17:19:08 | FBE6 | 68B | 0.8072
17:19:09 | FBDD | 68C | 0.8072
17:19:10 | FBDD | 68E | 0.8072
17:19:11 | FBE2 | 68B | 0.8072
17:19:11 | FBE1 | 68B | 0.8072
17:19:11 | FBE9 | 68D | 0.8072
17:19:11 | FBE8 | 68C | 0.8072
17:19:12 | FBDF | 68C | 0.8072
17:19:35 | FBDC | 791 | 0.9326
17:19:37 | FBD4 | 792 | 0.9326
17:19:39 | FBD1 | 792 | 0.9326
17:19:40 | FBCA | 78D | 0.9326
17:19:41 | FBC7 | 791 | 0.9326
17:19:42 | FBC2 | 78F | 0.9326
17:19:43 | FBCA | 791 | 0.9326
17:19:43 | FBC2 | 791 | 0.9326
17:19:43 | FBC4 | 790 | 0.9326
17:20:00 | FBB7 | 7C3 | 0.9565
17:20:00 | FBB2 | 7C3 | 0.9565
17:20:03 | FBC1 | 7C4 | 0.9565
17:20:03 | FBC3 | 7C1 | 0.9565
17:20:06 | FBCF | 7C4 | 0.9565
17:20:06 | FBD0 | 7C3 | 0.9565
17:20:06 | FBD6 | 7C5 | 0.9565
17:22:00 | FBE0 | 7EA | 0.9752
17:22:00 | FBDC | 7000000000 | 0.9752
17:22:00 | FBDF | 7000000000 | 0.9752
17:22:01 | FBE1 | 7ED | 0.9752
17:22:01 | FBDD | 7000000000 | 0.9752
17:22:02 | FBDF | 7000000000 | 0.9752
17:22:03 | FBE3 | 7EA | 0.9752
17:22:04 | FBDD | 7000000000 | 0.9752
17:22:05 | FBD7 | 7EA | 0.9752
17:22:05 | FBE1 | 7000000000 | 0.9752
17:22:06 | FBDA | 7000000000 | 0.9752
17:22:06 | FBD5 | 7EB | 0.9752
17:22:52 | FBEA | 7FF | 0.9865
17:22:52 | FBE3 | 7FF | 0.9865
17:22:52 | FBE7 | 7FF | 0.9865
17:22:52 | FBE2 | 7FF | 0.9865
17:22:52 | FBE2 | 7FF | 0.9865
17:22:53 | FBEA | 7FF | 0.9865
17:22:53 | FBEB | 7FF | 0.9865
17:22:53 | FBE9 | 7FF | 0.9865
17:22:53 | FBE6 | 7FF | 0.9865
17:22:53 | FBE7 | 7FF | 0.9865
17:22:53 | FBE5 | 7FF | 0.9865
17:22:54 | FBE3 | 7FF | 0.9865
17:22:54 | FBE3 | 7FF | 0.9865
17:22:54 | FBE2 | 7FF | 0.9865

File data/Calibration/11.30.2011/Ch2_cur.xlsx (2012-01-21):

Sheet: Ch1_cur.txt (root)
Root Name | Title | Author | Date/Time | Groups | Description
Ch1_cur.txt |  |  |  | 4
Group | Channels | Description | Anodization_Voltage | Anoidzation_Current | Board_Revision | Calibration_Version | Date_of_Testing | Electrolyte | GUI__Rev | Material | Researcher
Channel1 | 0 |  | 30.000000 | 100.000000 | 2.1 | 2.0 | 11/28/2011 | Liquid | 2.5 | Titanium | Michael DeLibero
Channel2 | 4 |  | 30.000000 | 100.000000 | 2.1 | 2.0 | 11/28/2011 | Liquid | 2.5 | Titanium | Michael DeLibero
Channel3 | 0 |  | 30.000000 | 100.000000 | 2.1 | 2.0 | 11/28/2011 | Liquid | 2.5 | Titanium | Michael DeLibero
Channel0 | 4
Channel1
Channel | Datatype | Unit | Length | Minimum | Maximum | Description | Start Index
Channel2
Channel | Datatype | Unit | Length | Minimum | Maximum | Description | NI_ArrayColumn | Start Index
Timestamp | DT_STRING |  | 79 |  |  |  | 0
Voltage | DT_STRING |  | 79 |  |  |  | 1
Current | DT_STRING |  | 79 |  |  |  | 2
Is | DT_STRING |  | 79 |  |  |  | 3
Channel3
Channel | Datatype | Unit | Length | Minimum | Maximum | Description | Start Index
Channel0
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

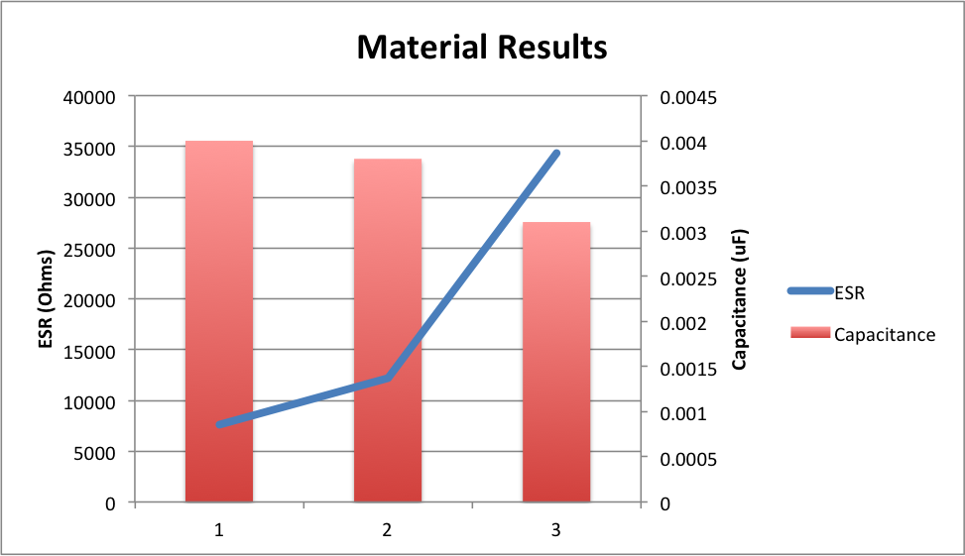
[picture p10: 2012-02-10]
ieeePaper/figures/materialResults.png

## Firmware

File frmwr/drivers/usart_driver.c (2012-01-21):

/* This file has been prepared for Doxygen automatic documentation generation.*/
/*! \file *********************************************************************
 *
 * \brief
 *      XMEGA USART driver source file.
 *
 *      This file contains the function implementations the XMEGA interrupt
 *      and polled USART driver.
 *
 *      The driver is not intended for size and/or speed critical code, since
 *      most functions are just a few lines of code, and the function call
 *      overhead would decrease code performance. The driver is intended for
 *      rapid prototyping and documentation purposes for getting started with
 *      the XMEGA ADC module.
 *
 *      For size and/or speed critical code, it is recommended to copy the
 *      function contents directly into your application instead of making
 *      a function call.
 *
 *      Some functions use the following construct:
 *          "some_register = ... | (some_parameter ? SOME_BIT_bm : 0) | ..."
 *      Although the use of the ternary operator ( if ? then : else ) is discouraged,
 *      in some occasions the operator makes it possible to write pretty clean and
 *      neat code. In this driver, the construct is used to set or not set a
 *      configuration bit based on a boolean input parameter, such as
 *      the "some_parameter" in the example above.
 *
 * \par Application note:
 *      AVR1307: Using the XMEGA USART
 *
 * \par Documentation
 *      For comprehensive code documentation, supported compilers, compiler
 *      settings and supported devices see readme.html
 *
 * \author
 *      Atmel Corporation: http://www.atmel.com \n
 *      Support email: avr@atmel.com
 *
 * $Revision: 1694 $
 * $Date: 2008-07-29 14:21:58 +0200 (ti, 29 jul 2008) $  \n
 *
 * Copyright (c) 2008, Atmel Corporation All rights reserved.
 *
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
 * 3. The name of ATMEL may not be used to endorse or promote products derived
 * from this software without specific prior written permission.
 *
 * THIS SOFTWARE IS PROVIDED BY ATMEL "AS IS" AND ANY EXPRESS OR IMPLIED
 * WARRANTIES, INCLUDING, BUT NOT LIMITED TO, THE IMPLIED WARRANTIES OF
 * MERCHANTABILITY AND FITNESS FOR A PARTICULAR PURPOSE ARE EXPRESSLY AND
 * SPECIFICALLY DISCLAIMED. IN NO EVENT SHALL ATMEL BE LIABLE FOR ANY DIRECT,
 * INDIRECT, INCIDENTAL, SPECIAL, EXEMPLARY, OR CONSEQUENTIAL DAMAGES
 * (INCLUDING, BUT NOT LIMITED TO, PROCUREMENT OF SUBSTITUTE GOODS OR SERVICES;
 * LOSS OF USE, DATA, OR PROFITS; OR BUSINESS INTERRUPTION) HOWEVER CAUSED AND
 * ON ANY THEORY OF LIABILITY, WHETHER IN CONTRACT, STRICT LIABILITY, OR TORT
 * (INCLUDING NEGLIGENCE OR OTHERWISE) ARISING IN ANY WAY OUT OF THE USE OF
 * THIS SOFTWARE, EVEN IF ADVISED OF THE POSSIBILITY OF SUCH DAMAGE.
 *****************************************************************************/
#include "usart_driver.h"
/*! \brief Initializes buffer and selects what USART module to use.
 *
 *  Initializes receive and transmit buffer and selects what USART module to use,
 *  and stores the data register empty interrupt level.
 *
 *  \param usart_data           The USART_data_t struct instance.
 *  \param usart                The USART module.
 *  \param dreIntLevel          Data register empty interrupt level.
 */
void USART_InterruptDriver_Initialize(USART_data_t * usart_data,
                                      USART_t * usart,
                                      USART_DREINTLVL_t dreIntLevel)
{
	usart_data->usart = usart;
	usart_data->dreIntLevel = dreIntLevel;

	usart_data->buffer.RX_Tail = 0;
	usart_data->buffer.RX_Head = 0;
	usart_data->buffer.TX_Tail = 0;
	usart_data->buffer.TX_Head = 0;
}


/*! \brief Set USART DRE interrupt level.
 *
 *  Set the interrupt level on Data Register interrupt.
 *
 *  \note Changing the DRE interrupt level in the interrupt driver while it is
 *        running will not change the DRE interrupt level in the USART before the
 *        DRE interrupt have been disabled and enabled again.
 *
 *  \param usart_data         The USART_data_t struct instance
 *  \param dreIntLevel        Interrupt level of the DRE interrupt.
 */
void USART_InterruptDriver_DreInterruptLevel_Set(USART_data_t * usart_data,
                                                 USART_DREINTLVL_t dreIntLevel)
{
	usart_data->dreIntLevel = dreIntLevel;
}

/*! \brief Test if there is data in the transmitter software buffer.
 *
 *  This function can be used to test if there is free space in the transmitter
 *  software buffer.
 *
 *  \param usart_data The USART_data_t struct instance.
 *
 *  \retval true      There is data in the receive buffer.
 *  \retval false     The receive buffer is empty.
 */
bool USART_TXBuffer_FreeSpace(USART_data_t * usart_data)
{
	/* Make copies to make sure that volatile access is specified. */
	uint8_t tempHead = (usart_data->buffer.TX_Head + 1) & USART_TX_BUFFER_MASK;
	uint8_t tempTail = usart_data->buffer.TX_Tail;

	/* There are data left in the buffer unless Head and Tail are equal. */
	return (tempHead != tempTail);
}



/*! \brief Put data (5-8 bit character).
 *
 *  Stores data byte in TX software buffer and enables DRE interrupt if there
 *  is free space in the TX software buffer.
 *
 *  \param usart_data The USART_data_t struct instance.
 *  \param data       The data to send.
 */
bool USART_TXBuffer_PutByte(USART_data_t * usart_data, uint8_t data)
{
	uint8_t tempCTRLA;
	uint8_t tempTX_Head;
	bool TXBuffer_FreeSpace;
	USART_Buffer_t * TXbufPtr;

	TXbufPtr = &usart_data->buffer;
	TXBuffer_FreeSpace = USART_TXBuffer_FreeSpace(usart_data);


	if(TXBuffer_FreeSpace)
	{
	  	tempTX_Head = TXbufPtr->TX_Head;
	  	TXbufPtr->TX[tempTX_Head]= data;
		/* Advance buffer head. */
		TXbufPtr->TX_Head = (tempTX_Head + 1) & USART_TX_BUFFER_MASK;

		/* Enable DRE interrupt. */
		tempCTRLA = usart_data->usart->CTRLA;
		tempCTRLA = (tempCTRLA & ~USART_DREINTLVL_gm) | usart_data->dreIntLevel;
		usart_data->usart->CTRLA = tempCTRLA;
	}
	return TXBuffer_FreeSpace;
}



/*! \brief Test if there is data in the receive software buffer.
 *
 *  This function can be used to test if there is data in the receive software
 *  buffer.
 *
 *  \param usart_data         The USART_data_t struct instance
 *
 *  \retval true      There is data in the receive buffer.
 *  \retval false     The receive buffer is empty.
 */
bool USART_RXBufferData_Available(USART_data_t * usart_data)
{
	/* Make copies to make sure that volatile access is specified. */
	uint8_t tempHead = usart_data->buffer.RX_Head;
	uint8_t tempTail = usart_data->buffer.RX_Tail;

	/* There are data left in the buffer unless Head and Tail are equal. */
	return (tempHead != tempTail);
}



/*! \brief Get received data (5-8 bit character).
 *
 *  The function USART_RXBufferData_Available should be used before this
 *  function is used to ensure that data is available.
 *
 *  Returns data from RX software buffer.
 *
 *  \param usart_data       The USART_data_t struct instance.
 *
 *  \return         Received data.
 */
uint8_t USART_RXBuffer_GetByte(USART_data_t * usart_data)
{
	USART_Buffer_t * bufPtr;
	uint8_t ans;

	bufPtr = &usart_data->buffer;
	ans = (bufPtr->RX[bufPtr->RX_Tail]);

	/* Advance buffer tail. */
	bufPtr->RX_Tail = (bufPtr->RX_Tail + 1) & USART_RX_BUFFER_MASK;

	return ans;
}



/*! \brief RX Complete Interrupt Service Routine.
 *
 *  RX Complete Interrupt Service Routine.
 *  Stores received data in RX software buffer.
 *
 *  \param usart_data      The USART_data_t struct instance.
 */
bool USART_RXComplete(USART_data_t * usart_data)
{
	USART_Buffer_t * bufPtr;
	bool ans;

	bufPtr = &usart_data->buffer;
	/* Advance buffer head. */
	uint8_t tempRX_Head = (bufPtr->RX_Head + 1) & USART_RX_BUFFER_MASK;

	/* Check for overflow. */
	uint8_t tempRX_Tail = bufPtr->RX_Tail;
	uint8_t data = usart_data->usart->DATA;

	if (tempRX_Head == tempRX_Tail) {
	  	ans = false;
	}else{
		ans = true;
		usart_data->buffer.RX[usart_data->buffer.RX_Head] = data;
		usart_data->buffer.RX_Head = tempRX_Head;
	}
	return ans;
}



/*! \brief Data Register Empty Interrupt Service Routine.
 *
 *  Data Register Empty Interrupt Service Routine.
 *  Transmits one byte from TX software buffer. Disables DRE interrupt if buffer
 *  is empty. Argument is pointer to USART (USART_data_t).
 *
 *  \param usart_data      The USART_data_t struct instance.
 */
void USART_DataRegEmpty(USART_data_t * usart_data)
{
	USART_Buffer_t * bufPtr;
	bufPtr = &usart_data->buffer;

	/* Check if all data is transmitted. */
	uint8_t tempTX_Tail = usart_data->buffer.TX_Tail;
	if (bufPtr->TX_Head == tempTX_Tail){
	    /* Disable DRE interrupts. */
		uint8_t tempCTRLA = usart_data->usart->CTRLA;
		tempCTRLA = (tempCTRLA & ~USART_DREINTLVL_gm) | USART_DREINTLVL_OFF_gc;
		usart_data->usart->CTRLA = tempCTRLA;

	}else{
		/* Start transmitting. */
		uint8_t data = bufPtr->TX[usart_data->buffer.TX_Tail];
		usart_data->usart->DATA = data;

		/* Advance buffer tail. */
		bufPtr->TX_Tail = (bufPtr->TX_Tail + 1) & USART_TX_BUFFER_MASK;
	}
}


/*! \brief Put data (9 bit character).
 *
 *  Use the function USART_IsTXDataRegisterEmpty before using this function to
 *  put 9 bit character to the TX register.
 *
 *  \param usart      The USART module.
 *  \param data       The data to send.
 */
void USART_NineBits_PutChar(USART_t * usart, uint16_t data)
{
	if(data & 0x0100) {
		usart->CTRLB |= USART_TXB8_bm;
	}else {
		usart->CTRLB &= ~USART_TXB8_bm;
	}

	usart->DATA = (data & 0x00FF);
}


/*! \brief Get received data (9 bit character).
 *
 *  This function reads out the received 9 bit character (uint16_t).
 *  Use the function USART_IsRXComplete to check if anything is received.
 *
 *  \param usart      The USART module.
 *
 *  \retval           Received data.
 */
uint16_t USART_NineBits_GetChar(USART_t * usart)
{
	if(usart->CTRLB & USART_RXB8_bm) {
		return(0x0100 | usart->DATA);
	}else {
		return(usart->DATA);
	}
}

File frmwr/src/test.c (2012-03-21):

// Author:	Michael DeLibero
// Date Created:	10.27.2011

// This file contains all of the unit testing functions for the AnodeV3.0 proj
//-----------------------------------------------------------------------------
// #includes
#include <avr/io.h>
#include "test.h"
#include "init.h"
#include "TC_driver.h"
#include "spi.h"
#include "spi_driver.h"
#include "dac.h"
#include "usart.h"
#include "adc.h"
#include "adc_driver.h"
//-----------------------------------------------------------------------------
// Defines
#define LEDPORT		(PORTF)
//-----------------------------------------------------------------------------
// Variable Definitions and Declarations
volatile testing_flags_t testing_flags;
//dac
	volatile uint16_t dac_cnt    = 0b0011111111;
	volatile uint16_t dac_cntMax = 0b1111111111; // 10 bits ---(73,300,775,185) 
	volatile int ch_num = 1;
	uint8_t receivedData[NUM_SPI_BYTES];
	SPI_DataPacket_t dataPacket;
	uint8_t sendData[NUM_SPI_BYTES];
	volatile uint8_t EN = 1;
	volatile uint8_t low_byte;
	volatile uint8_t hi_byte;
	volatile uint8_t status;
	PORT_t *ss_port = &PORTF;
	volatile unsigned int ss_pin = PIN0_bm;
//usart
	volatile char rxByte = 0x33; // stores the last byte read by the usart rx.
//-----------------------------------------------------------------------------
//-----------------------------------------------------------------------------
// Functions
//-----------------------------------------------------------------------------
//-----------------------------------------------------------------------------
void led_test(void) {
	led0 = 0;
	led1 = 1;
	led2 = 1;
	led3 = 0;
}
//-----------------------------------------------------------------------------
void clk_test(void) {	
	LEDPORT.DIRSET = 0xFF; // Set Port F pins as output
	LEDPORT.OUTSET = 0x80; // Sets the values on port F pins
	TCC0.CTRLA = TC_CLKSEL_DIV1024_gc; // Set clock prescaler (14.12.1)
	TCC0.PER = 1563; // Set Clock period to 9.99Hz
	TCC0.INTCTRLA = TC_OVFINTLVL_LO_gc; // enable timer overflow int and
		// set its priority to low 
	sei(); // enable global interrupts
	PMIC.CTRL = PMIC_LOLVLEN_bm; // Enable Low Level interrupts (12.8.3)
	
	while (1)
	{
		LEDPORT.OUTTGL = 0x10; // Toggle led
	}
}
//-----------------------------------------------------------------------------
void usart_test(void) {
	USARTF0.DATA = 0x0F; // necessary to trip the interrupt once the usart
						// flag has been set.
	while(1) {nop();}
}
		
void usartTx_test(void) {		
	USARTF0.DATA = 0x7E;
} // end	usartTx_test()

void usartRx_test(void) {
	rxByte = USARTF0.DATA;	
}
//-----------------------------------------------------------------------------
void usartRxMsg_test(volatile char uRxByte) {
	static uint8_t ind = 0;
	
	*dat2pc_p[ind] = uRxByte;
	
	ind++;
	if (ind >= 12) {
		ind = 0;
	}
}
//-----------------------------------------------------------------------------
void dac_test(void)  {
	#define sweep	(1) // 0 --- sweep output, 1 --- const output
	
	ch[ch1].vol2dac_u.all = 0x02C1;
	ch[ch2].vol2dac_u.all = 0x02C1;
	
	ch[ch1].cur2dac_u.all = 0x02C1;
	ch[ch2].cur2dac_u.all = 0x02C1;
	
	bool vol_1_sweep = false;
	bool vol_2_sweep = false;
	bool cur_1_sweep = false;
	bool cur_2_sweep = false;
	
	if (vol_1_sweep == false) {
		dac_up(DAC_VOL,GA_2x,SHDN_n,ch1,&ch[0]);
	}
	if (vol_2_sweep == false){
		dac_up(DAC_VOL,GA_2x,SHDN_n,ch2,&ch[0]);
	}		
	if (cur_1_sweep == false){
		dac_up(DAC_CUR,GA_1x,SHDN_n,ch1,&ch[0]);
	}
	if (cur_2_sweep == false) {
		dac_up(DAC_CUR,GA_1x,SHDN_n,ch2,&ch[0]);
	}
} // end	void dac_test(void)  {
//-----------------------------------------------------------------------------
void spiInit_test(void) {
	// This is a stripped down version of dac_up(...)
	uint8_t spiRx[NUM_SPI_BYTES]; 
		//data rx at Xmega SPI port -- var is only a placeholder.
	uint8_t spiTx[NUM_SPI_BYTES];
		 // formatted for ext daqs to be sent from the mega SPI port.
	SPI_DataPacket_t spi_fdata; 
		// data packet formatted for Xmega to be sent from the mega SPI port.
	
	spiTx[0] = 0x32;
	spiTx[1] = 0x87;
	
	SPI_MasterCreateDataPacket(&spi_fdata,
                                spiTx,
                                spiRx,
                                NUM_SPI_BYTES,
                                ch[ch_num].ss_port,
                                ch[ch_num].ss_pin);
								
								
	uint8_t status;
	do {
		status = SPI_MasterInterruptTransceivePacket(&spiMasterC,&spi_fdata);	
	} while (status != SPI_OK);
		
	/* Wait for transmission to complete. */
	while (spi_fdata.complete == false) {
	}
} // end    void spiInit_test(void) {
//-----------------------------------------------------------------------------
void adcOff_test(void) {
// This exports the offsets to channel 1 and 2 voltage.
// Look at these on your PC to make sure that they seem reasonable.
// Also make sure that the adc ISR is disabled when this function flag is 
// active or the offsets will be overwritten.
	while(1) {
		ch[ch1].volfadc_u.all = ADC_Offset_Get_Signed(&ADCA, &(ADCA.CH2), true);
		ch[ch2].volfadc_u.all = ADC_Offset_Get_Signed(&ADCB, &(ADCB.CH2), true);
		
		delay_us(500);
	}	
}
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

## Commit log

2012-01-21 included all files
    [AnodV2.0.brd, AnodV2.0.sch, AnodV2.1.brd, AnodV2.1.sch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]
2012-01-26 ui: -- check user parameters
    [PartList.xlsx, PartList_10v27v2011.xlsx, PartList_12v16v2011.xlsx, purRec_Digikey_01.24.2012.xlsx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]
2012-01-31 started code to log test data
    [test_file.xls]
2012-01-31 created file hierarchy for project
    [usr_info.xls, usr_info_template.xls]
2012-01-31 Deleted unneeded files
    [test_file.xls, usr_info.xls, usr_info_template.xls]
2012-01-31 started working on testing testConfig parameter limits
    [testConfig.xls, testConfig_template.xls]
2012-01-31 'Worked on testing testConfig parameter limits'
    [PartList.xlsx, PartList_10v27v2011.xlsx, PartList_12v16v2011.xlsx, purRec_Digikey_01.24.2012.xlsx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]
2012-02-01 Error - numbers stored in testConfig_template.xls are being stored as text
    [testConfig.xls, testConfig_template.xls]
2012-02-01 fixed testConfig_template.xls error -- numbers are now stored as floats
    [testConfig.xls, testConfig_template.xls]
2012-02-01 code now sucessfully tests that the testConfig parameters are below their limits. Edge cases are not tested
    [testConfig.xls]
2012-02-01 changed rheaders and data to testParam_name and testParam_val
    [testConfig.xls]
2012-02-02 changed vars to a single dictionary - testParam
    [testConfig.xls, testConfig_template.xls]
2012-02-02 Finished initial coding of init().
    [testConfig_template.xls]
2012-02-02 Made state a namedtuple that gets passed between functions.
    [testConfig.xls]
2012-02-03 Started to change the data structure of the state variable. Currently broken.
    [testConfig.xls]
2012-02-09 Added Current Source outline and began writing from it.
2012-02-09 1st draft of describing the ideal and real current source.
2012-02-09 added dicscretizition error subsection to current source limitations section.
2012-02-09 added pass diode error subsection to current source limitations section.
2012-02-09 Added outline for next verision of the introduction. Focusing more on titanium capacitors and the instrumentation this time.
2012-02-10 added Lauries data
    [capData_Laurie.xlsx]
2012-02-10 Created section describing overall circuitry
2012-02-11 Inserted sample bibliograhy. Began editing content again.
2012-03-02 Finished and tested matches_template()
    [testConfig.xls]
2012-03-02 finished testing and validating check_usr_limits()
    [testConfig.xls]
2012-03-05 finished and tested creatState() function
    [testConfig.xls]
2012-03-09 changed state time from min to sec. Tested timer for 1 min loop on both channels.
    [testConfig.xls]
2012-03-20 current fmwr outputs 0xE7 constantly
2012-03-21 added file to spoof communication with the board
2012-03-22 program writes dummy data to .txt file
    [testConfig.xls]
2012-03-23 program now is capped at 60000 samples
    [testConfig.xls]
2012-03-23 started to code post processing funs
    [testConfig.xls]
2012-03-24 wrote and tested createFile() --> creates and formats .xls file for data insertion
    [testConfig.xls]
2012-03-24 main loop now runs post proc. current error in postproc
2012-03-24 finished 1st rev of ui spoofing data. Need to add in provisions for real board
2012-04-13 small changes
    [capData_Laurie.xlsx]
2012-04-16 added future work section decribed software control loop to control power dissipated in pass transistor.
